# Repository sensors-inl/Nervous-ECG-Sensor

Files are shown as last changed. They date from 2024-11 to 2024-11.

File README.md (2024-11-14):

# Nervous - ECG Sensor

The **Nervous** initiative is a project embracing open-hardware and open-source
principles, with the goal of delivering wearable sensors and accompanying
software for the analysis of Autonomic Nervous System (SNA) activity.

The entire project is published under the MIT Licence.

## ECG Sensor

Contained within this repository are ECAD files for the production of PCBs and
the assembly of circuits for a wireless, wrist-worn ECG sensor.

Originally intended for measuring heart rate via electrodes positioned on the
forearms or hands, this sensor utilizes the AD8232 in conjunction with passive
components, as outlined in the "EXERCISE APPLICATION: HEART RATE MEASURED AT
THE HANDS" section on page 27 of the datasheet:
<https://www.analog.com/media/en/technical-documentation/data-sheets/ad8232.pdf>.
You have the freedom to adjust this configuration to suit different
applications and electrode placements.

The microcontroller employed is an ISP1807 (Insight SiP), which houses a
nRF52840 (Nordic Semiconductor).

## Hardware features

- USB-C connector for charging battery
- Embedded LiPo battery charger and I2C fuel-gauge
- On/Off SPST button (enables / disables voltage regulator)
- RGB status Led
- AD8232 ECG AFE featuring a 7 Hz - 24 Hz bandpass filter (56 dB @ 13 Hz) and
RLD
- BLE wireless communication

## Manufacturing and assembling

Gerber files, drill files, assembly drawings, pick-and-place files, and the
Bill of Materials (BOM) are accessible in the ```Export``` folder:

- ```Export/Manufacturing```: Gerber (.gbr) and Drill files (.drl)
- ```Export/Assembly```: Assembly drawing (.pdf), pick and place files (.pos),
BOM (.csv)

### PCB properties for manufacturing

|                          |                   |
| :----------------------- | :---------------: |
| Dimensions               | 21.5 mm x 33.5 mm |
| Number of layers         | 2                 |
| Minimal insulation width | 0.150 mm          |
| Minimal trace width      | 0.150 mm          |
| Miniaml hole size        | 0.200 mm          |

## Modification

The ```Source``` folder holds the original KiCad project, designed using KiCad
version 7.0.8.

## Note on cables and electrodes placement

This sensor is designed to capture ECG signals across various conditions while minimizing discomfort for the subject.
To achieve this, it incorporates high gain to accommodate electrode placement on the hands or forearms, where signal strength is typically lower.
However, this positioning also amplifies sensitivity to motion artifacts, which can interfere with accurate heart beat detection.
To mitigate the impact of these artifacts, we recommend utilizing solid gel electrodes like the 3M 2650.
For connectivity, we implemented a simple 2.54 mm, 3-way header on the sensor, allowing for custom electrode connections.
It's advised to use short cables for connecting the two electrodes in proximity to the device (RLD and RA), and a longer cable for the third electrode on the opposite arm (LA).
We constructed cables featuring female crimp terminals on the sensor end and 3 mm banana plugs with a snap adapter on the electrode end.
Finally, securely hold the electrodes in place, along with the cables near the electrodes, using medical tape to minimize noise from connector friction.

## Authors and contact

- Authors: Bertrand Massot, Matthieu Mesnage, Hugo Buy
- Affiliation: INSA Lyon, Ecole Centrale Lyon, Universite Claude Bernard Lyon
1, CPE Lyon, CNRS, INL UMR 5270, 69600 Villeurbanne France.
- Contact email: <bertrand.massot@insa-lyon.fr>

## Funding

This work was supported the French National Reasearch Agency (ANR) under the
grant ANR-22-CE31-0023-03 RENFORCE.

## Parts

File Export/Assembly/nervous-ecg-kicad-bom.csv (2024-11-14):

Id | Quantity | Designator | Description | Manufacturer | Manufacturer Part Number | Supplier | Supplier Part Number
1 | 1 | BT1 | BATT LI-PO 3.7V 165MAH | BAK TECHNOLOGY | LP-402025-1S-3 | FARNELL | 2077885
2 | 5 | C1, C2, C6, C8, C9 | CAP CER 1UF 10V X5R 0402 | Yageo | CC0402KRX5R6BB105 | Farnell | 1458896
3 | 2 | C3, C4 | CAP CER 4.7UF 6.3V X5R 0402 | Yageo | CC0402KRX5R5BB475 | Farnell | 3369135
4 | 1 | C5 | CAP CER 0.47UF 10V X5R 0402 | Yageo | CC0402KRX5R6BB474 | Farnell | 3369138
5 | 3 | C7, C11, C13 | CAP CER 0.1UF 16V X7R 0402 | Yageo | CC0402JRX7R7BB104 | Farnell | 3369125
6 | 1 | C10 | CAP CER 1000PF 50V X7R 0402 | Yageo | CC0402KRX7R9BB102 | Farnell | 3019380
7 | 2 | C12, C14 | CAP CER 0.22UF 10V X5R 0402 | Yageo | CC0402KRX5R6BB224 | Farnell | 9402055
8 | 1 | C15 | CAP CER 22000PF 16V X7R 0402 | Yageo | CC0402KRX7R7BB223 | Farnell | 3019299
9 | 1 | C16 | CAP CER 3300PF 50V X7R 0402 | Yageo | CC0402KRX7R9BB332 | Farnell | 3873402
10 | 1 | D1 | DIODE SCHOTTKY 20V 500MA SOD123 | STMicroelectronics | STPS0520Z | FARNELL | 1467545
11 | 2 | D4, D5 | LED RGB CLEAR 4SMD | KINGBRIGHT | APHF1608LSEEQBDZGKC | DIGIKEY | 754-2143-1-ND
12 | 1 | F1 | PTC RESET FUSE 16V 500MA 1210 | BEL | 0ZCH0050FF2G | Farnell | 2848519
13 | 1 | J1 | CONN RCP USB3.1 TYPEC 24P SMD RA | MOLEX | 105450-0101 | FARNELL | 2524076
14 | 1 | J2 | MOLEX 53048-0310 | MOLEX | 53048-0310 | FARNELL | 9732918
15 | 1 | J4 | CONN HEADER R/A 4POS 2.54MM | AMPHENOL COMMUNICATIONS SOLUTIONS | 77315-118-04LF | FARNELL | 3728851
16 | 1 | R1 | RES SMD 3K OHM 1% 1/16W 0402 | Yageo | AC0402FR-073KL | Farnell | 3951323
17 | 1 | R3 | RES 5.9K OHM 1% 1/16W 0402 | Yageo | RC0402FR-075K9L | Farnell | 3951010
18 | 6 | R5, R6, R7, R8, R10, R14 | RES 10K OHM 1% 1/16W 0402 | Yageo | RC0402FR-0710KL | Farnell | 9239359
19 | 1 | R9 | RES 0.01 OHM 1% 1/10W 0603 | Yageo | RL0603FR-070R01L | Farnell | 8067767
20 | 5 | R11, R12, R13, R18, R19 | RES SMD 10M OHM 1% 1/16W 0402 | Yageo | RC0402FR-0710ML | Farnell | 1458733
21 | 2 | R15, R16 | RES SMD 180K OHM 1% 1/10W 0402 | Panasonic | ERJ-H2RF1803X | Farnell | 3644222
22 | 1 | R17 | RES SMD 360K OHM 1% 1/16W 0402 | Yageo | RC0402FR-07360KL | Digi-Key | 311-360KLRCT-ND
23 | 3 | R20, R21, R27 | RES SMD 1M OHM 1% 1/16W 0402 | Yageo | RC0402FR-071ML | Farnell | 9239588
24 | 3 | R22, R24, R30 | RES 1K OHM 1% 1/16W 0402 | Yageo | RC0402FR-071KL | Farnell | 9239235
25 | 2 | R23, R25 | RES 100K OHM 1% 1/16W 0402 | Yageo | RC0402FR-07100KL | Farnell | 9239472
26 | 2 | R26, R32 | RES 4.7K OHM 1% 1/16W 0402 | Yageo | RC0402FR-074K7L | Farnell | 9239316
27 | 1 | R28 | RES 5.1K OHM 0.5% 1/10W 0402 | PANASONIC | ERJ-U2RD5101X | FARNELL | 3516311
28 | 1 | R29 | RES 5.1K OHM 0.5% 1/10W 0402 | PANASONIC | ERJ-U2RD5101X | FARNELL | 3516311
29 | 1 | U1 | RF TXRX MODULE BT TRACE ANT SMD | INSIGHT SIP | ISP1807-LR-RS | DIGIKEY | 1786-1019-1-ND
30 | 1 | U2 | IC BATT CHG LI-ION 1CELL 16QFN | TEXAS INSTRUMENTS | BQ24074RGTT | FARNELL | 3123775
31 | 1 | U3 | IC BATT FUEL GAUGE LICOO2 12SON | TEXAS INSTRUMENTS | BQ27441DRZR-G1A | FARNELL | 3123775
32 | 1 | U4 | IC REG LINEAR 3.3V 200MA SOT23-5 | TEXAS INSTRUMENTS | TPS7A0533PDBVR | DIGIKEY | 296-TPS7A0533PDBVRDKR-ND
33 | 1 | U5 | IC ECG FRONT END 20LFCSP | Analog Devices | AD8232ACPZ-R7 | Farnell | 4029748
34 | 1 | U6 | IC INTFACE SPECIALIZED TSOT23-6 | ANALOG DEVICES | MAX16054AZT+T | FARNELL | 2515822
35 | 1 | U7 | SWITCH TACTILE SPST-NO 0.02A 15V | PANASONIC | EVP-AA502W | FARNELL | 2831733
36 | 1 | U9 | TVS Diode WE-TVS-Standard, VRWM=5.0V | SEMTECH | SM05.TCT | Farnell | 1456392
37 | 1 | U10 | LIGHTPIPE PNL MT CONVEX 0.250" | DIALIGHT | 515-1302-0250F | FARNELL | 3775816

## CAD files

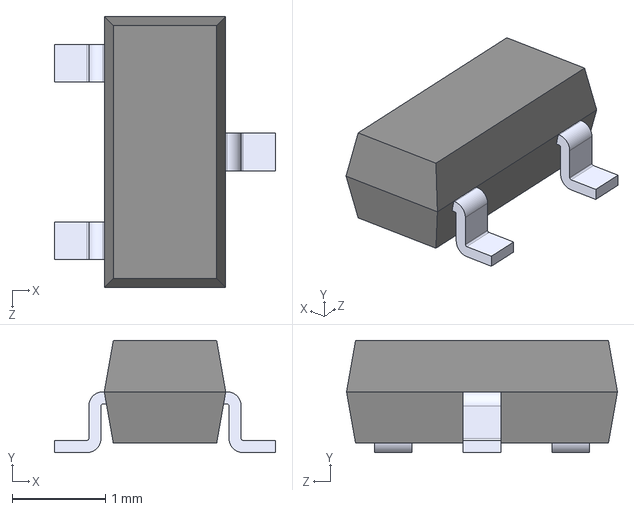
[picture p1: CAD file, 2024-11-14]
Source/nervous-ecg-3dmodels/SM05.TCT.STEP
2.37 x 1.20 x 2.90 mm

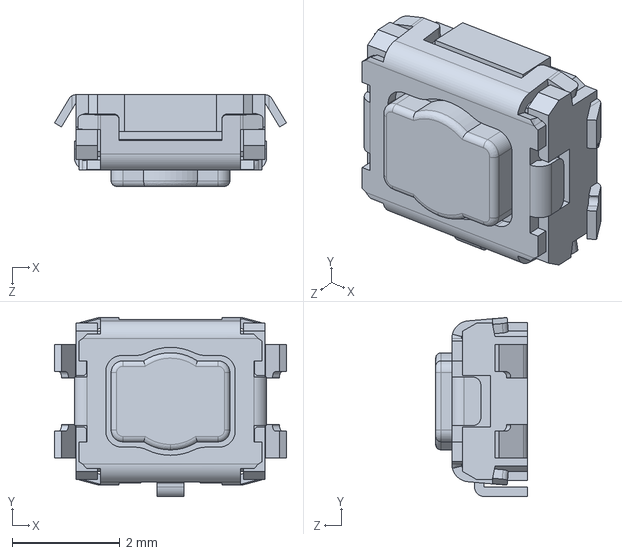
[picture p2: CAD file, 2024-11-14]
Source/nervous-ecg-3dmodels/EVPAA-102K_302K_502W_702W_902Q.STEP
4.30 x 3.32 x 1.70 mm

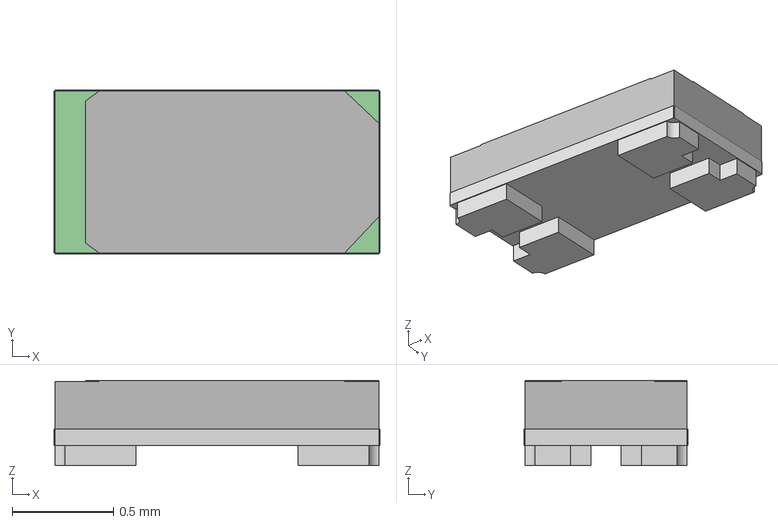
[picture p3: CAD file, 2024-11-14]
Source/nervous-ecg-3dmodels/LED_RGB_SMD_0603.step
1.61 x 0.81 x 0.42 mm

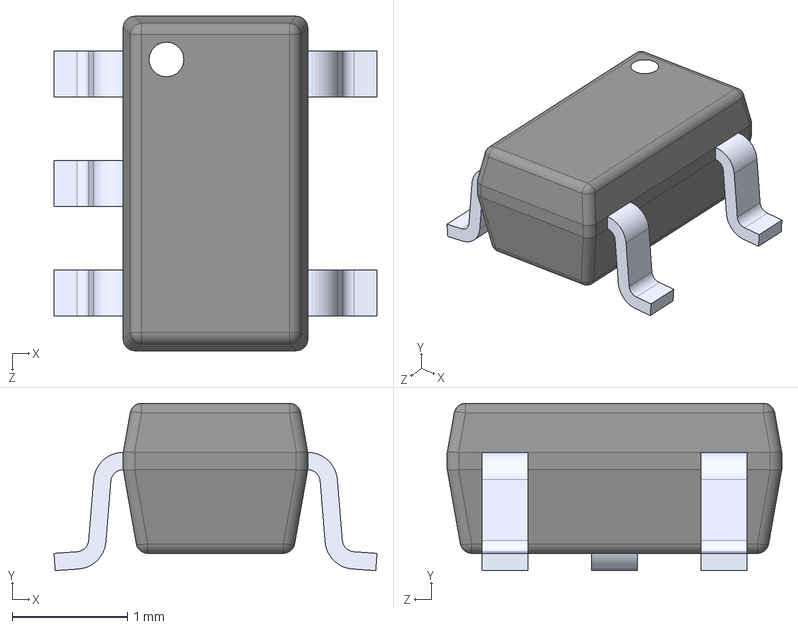
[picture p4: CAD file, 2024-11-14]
Source/nervous-ecg-3dmodels/TPS7A0533PDBVR.step
2.80 x 1.45 x 2.90 mm

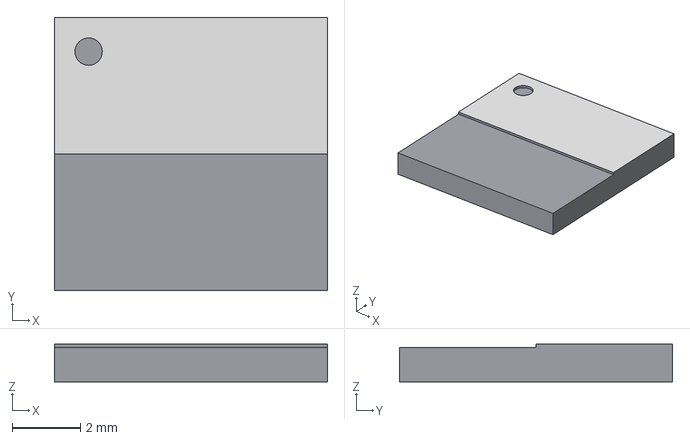
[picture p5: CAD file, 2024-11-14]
Source/nervous-ecg-3dmodels/ISP1807-LR.step
8.00 x 8.00 x 1.10 mm

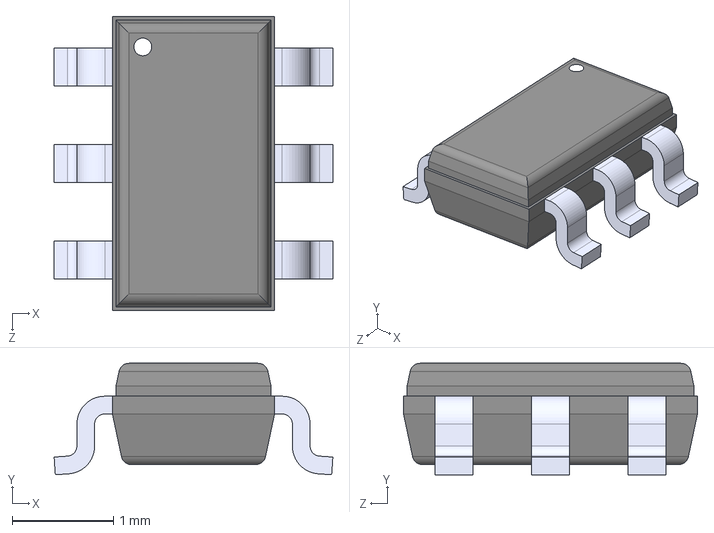
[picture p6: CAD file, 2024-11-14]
Source/nervous-ecg-3dmodels/MAX16054AZT+T.STEP
2.75 x 1.10 x 2.90 mm

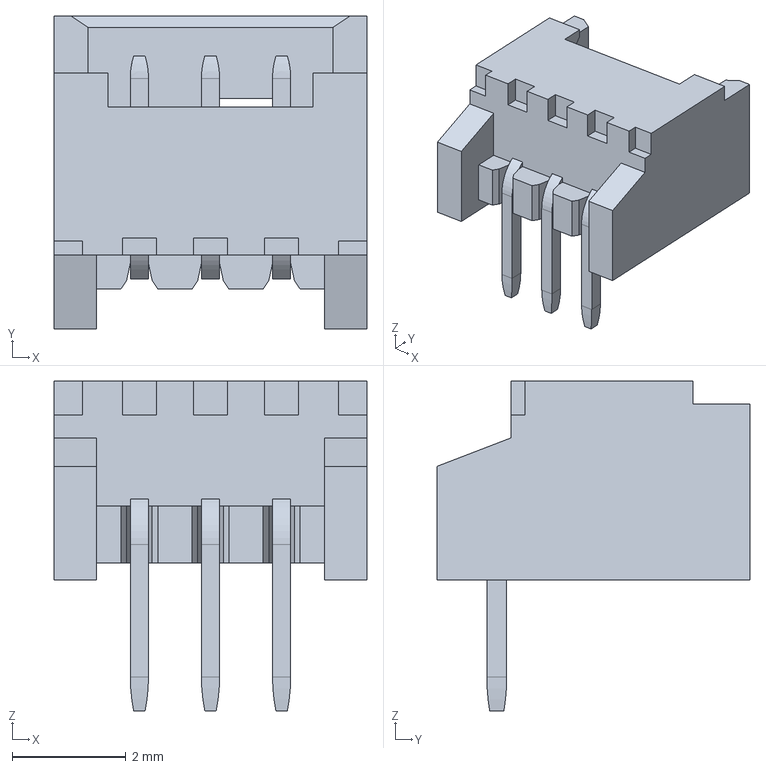
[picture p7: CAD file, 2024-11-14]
Source/nervous-ecg-3dmodels/530480310.stp
5.50 x 5.50 x 5.80 mm

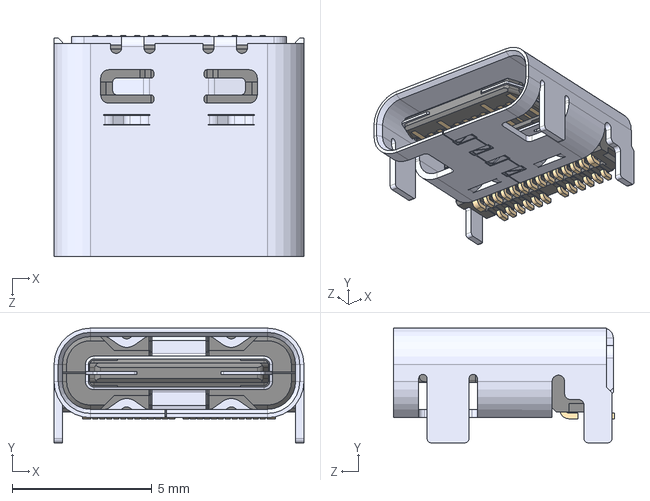
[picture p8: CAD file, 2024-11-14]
Source/nervous-ecg-3dmodels/105450-0101.step
8.94 x 4.10 x 7.90 mm

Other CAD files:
Housing/nervous-housing.f3z

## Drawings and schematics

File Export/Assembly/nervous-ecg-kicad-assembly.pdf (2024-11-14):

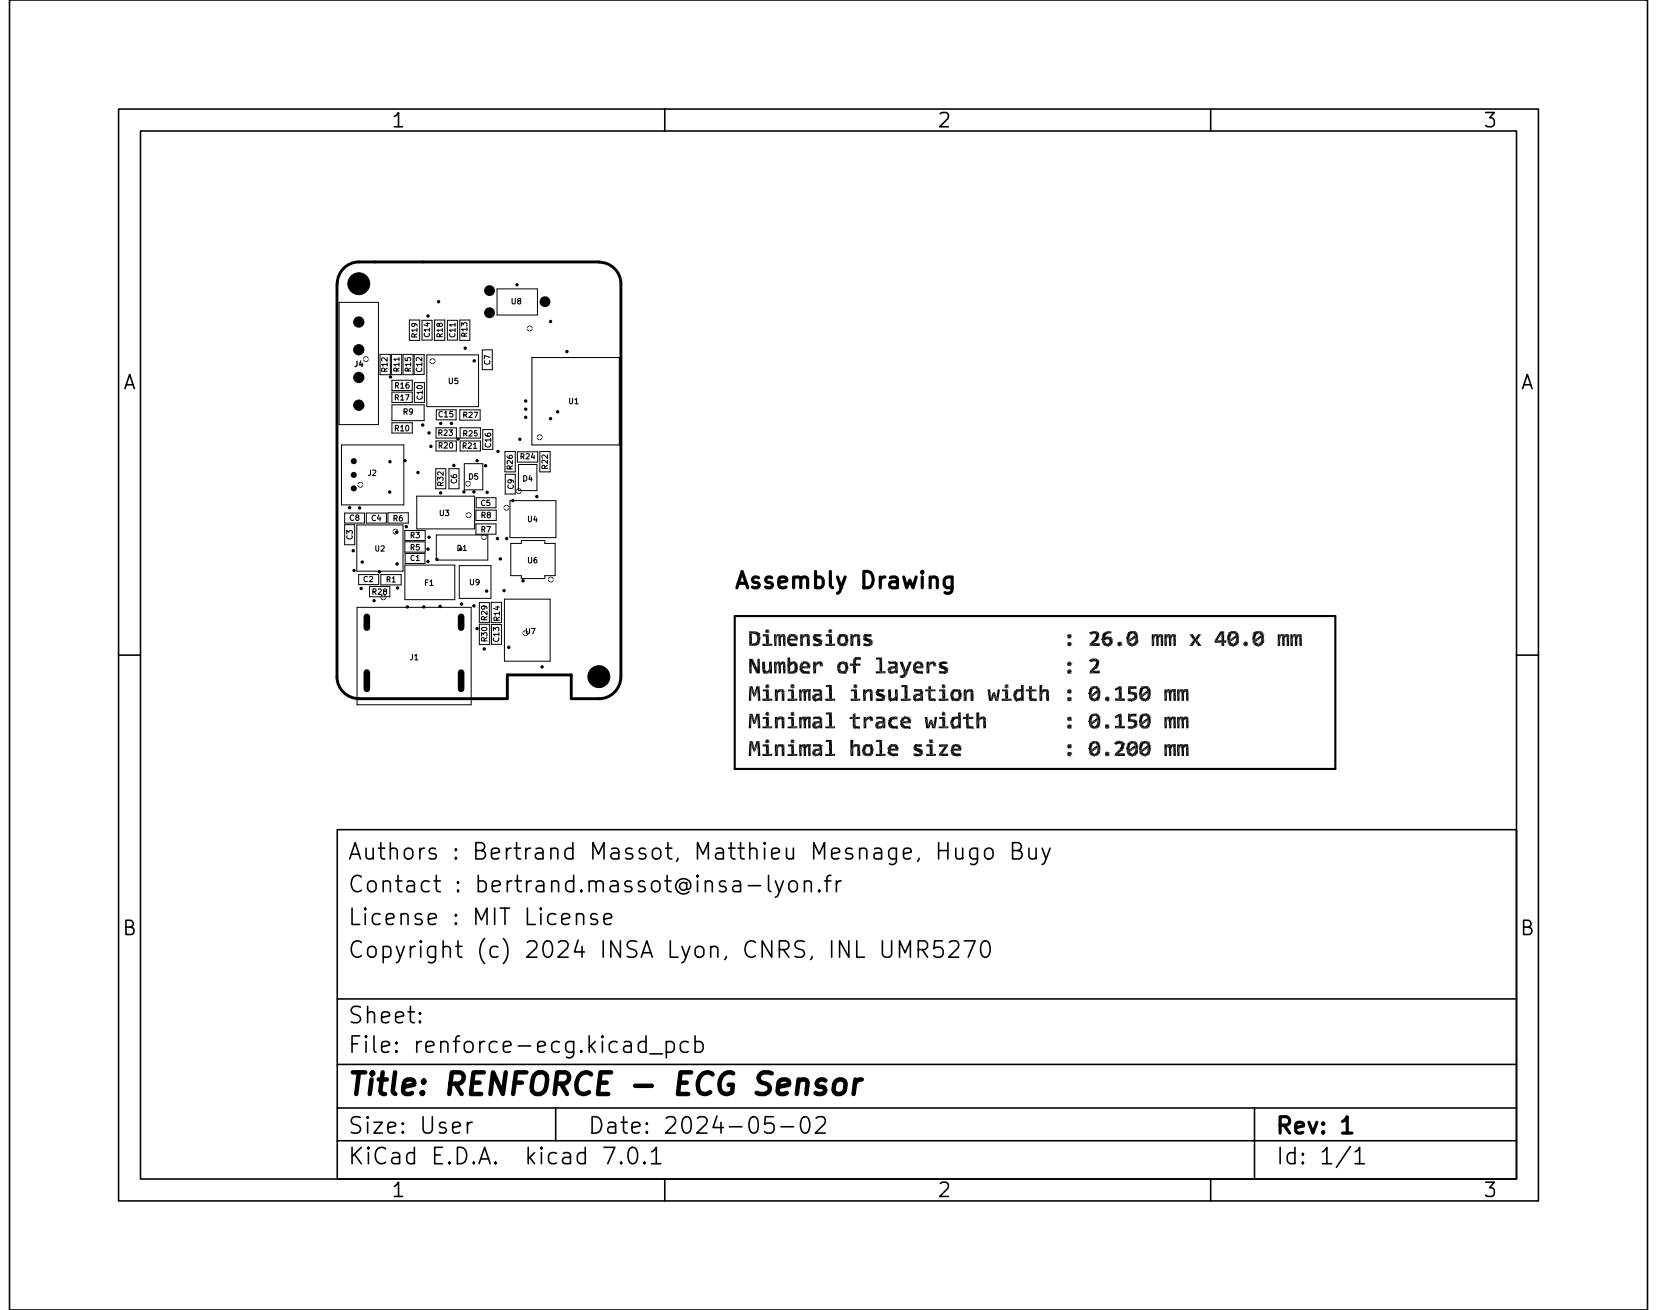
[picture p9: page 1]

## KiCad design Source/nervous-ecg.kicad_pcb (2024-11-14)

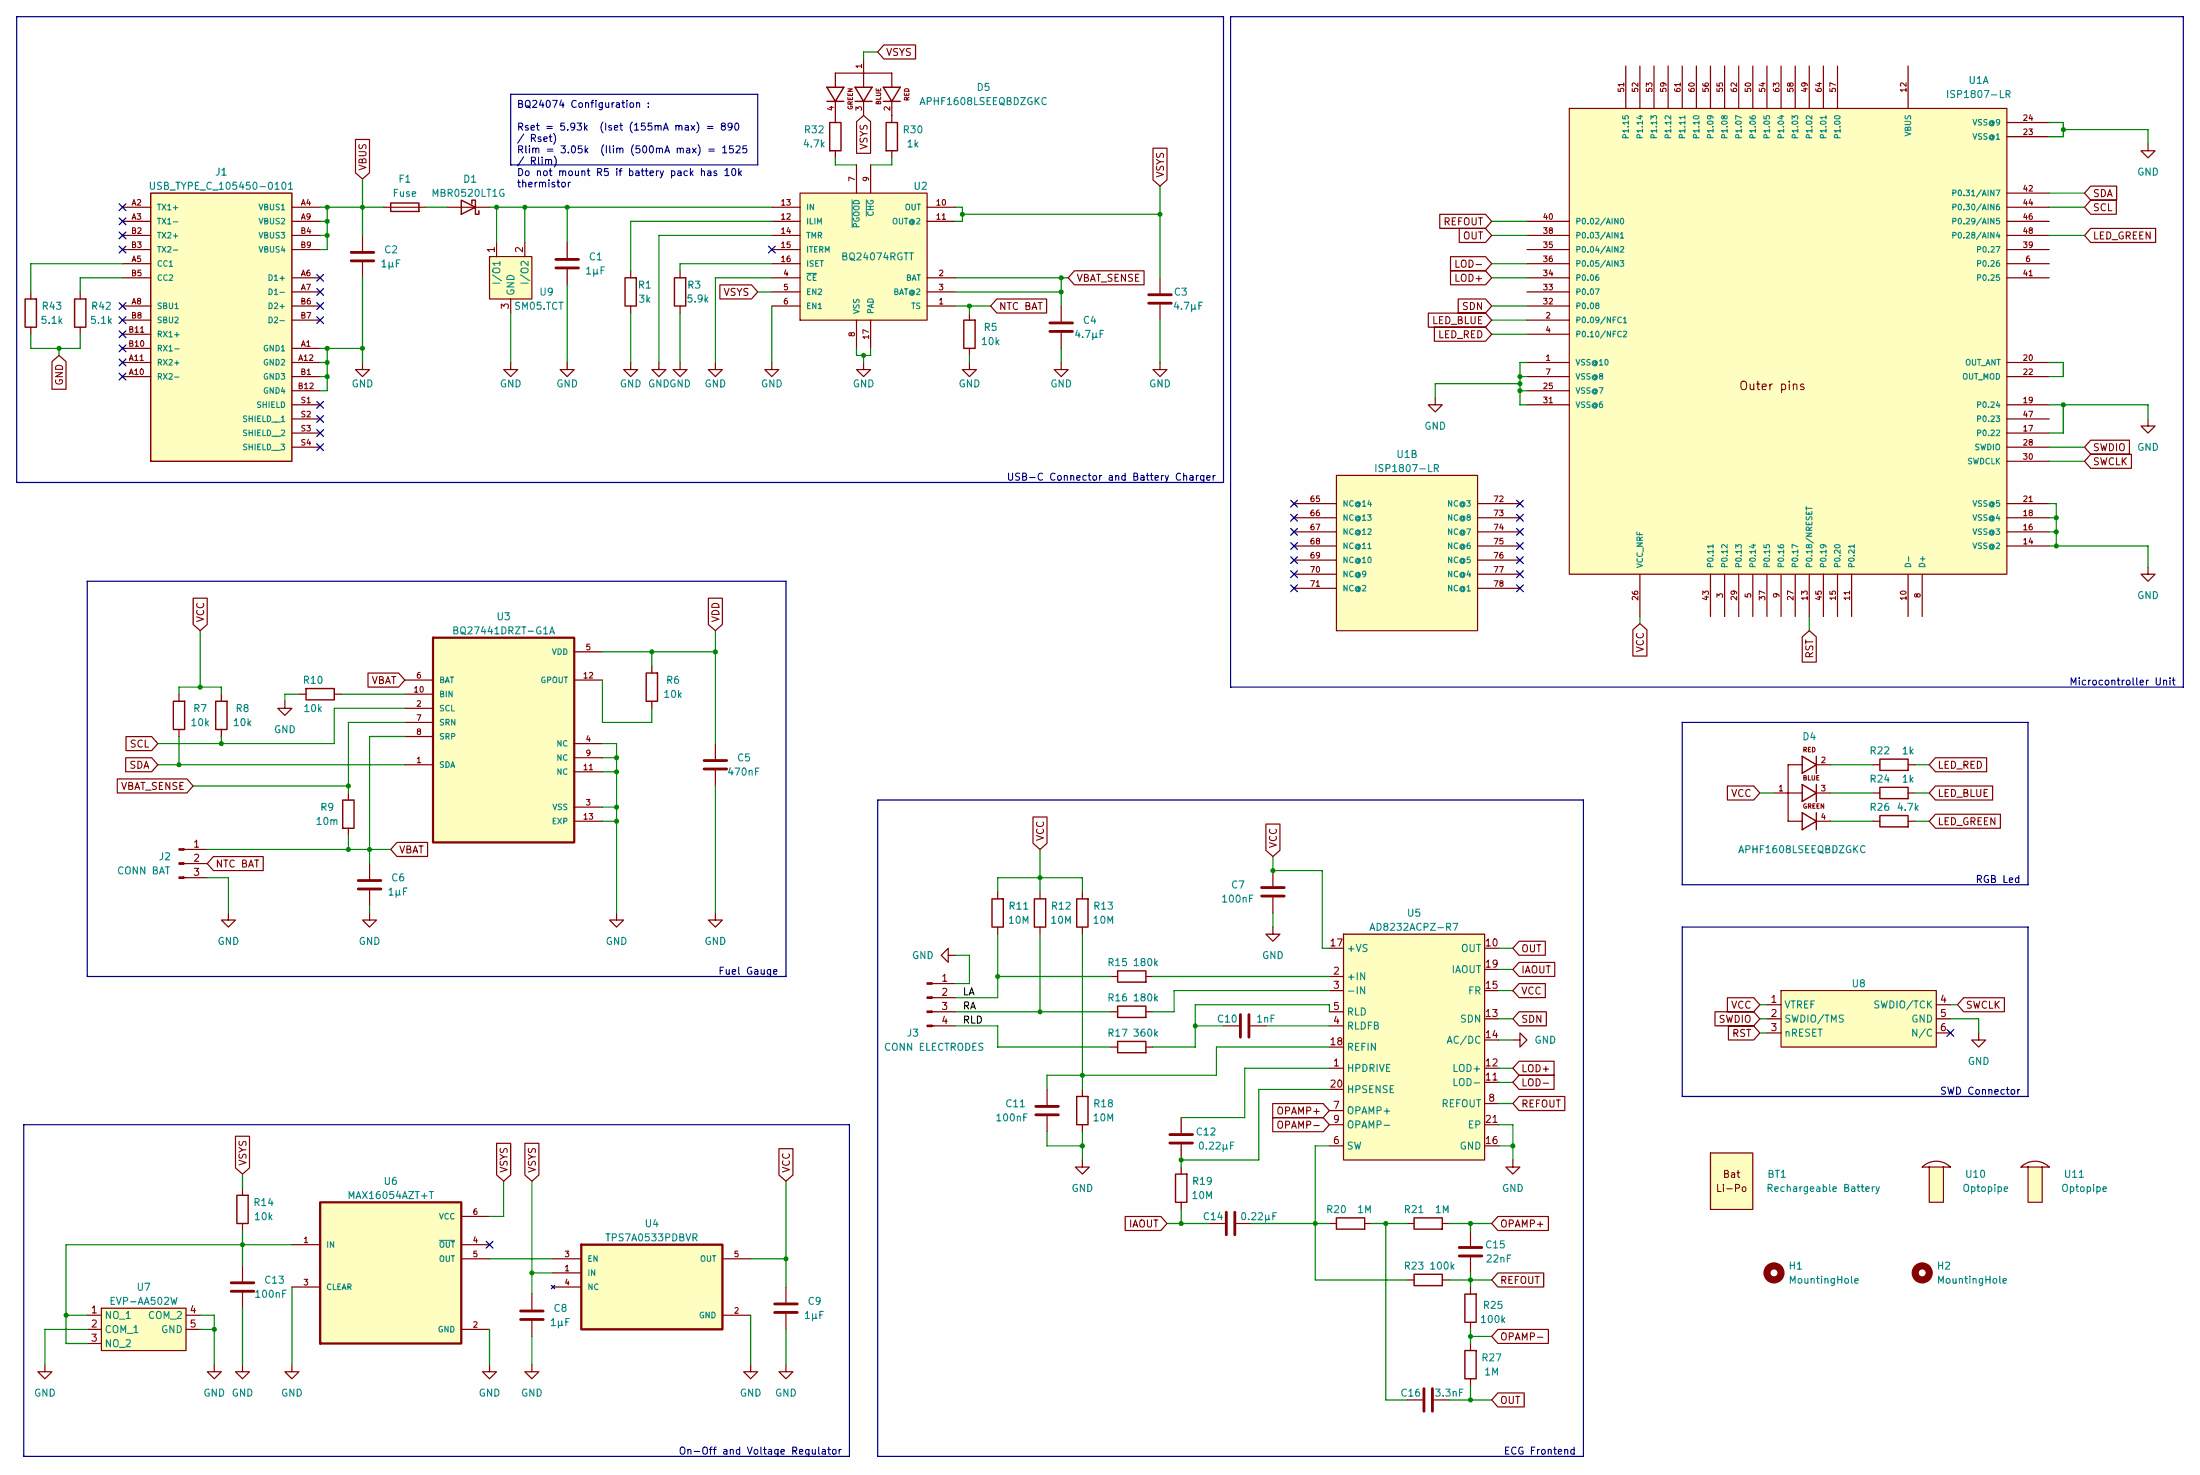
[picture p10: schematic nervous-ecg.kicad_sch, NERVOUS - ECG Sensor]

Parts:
BT1: BATT LI-PO 3.7V 165MAH; Manufacturer Part Number LP-402025-1S-3
C1, C2, C6, C8, C9: CAP CER 1UF 10V X5R 0402; C_0402_1005Metric; Manufacturer Part Number CC0402KRX5R6BB105
C3, C4: CAP CER 4.7UF 6.3V X5R 0402; C_0402_1005Metric; Manufacturer Part Number CC0402KRX5R5BB475
C5: CAP CER 0.47UF 10V X5R 0402; C_0402_1005Metric; Manufacturer Part Number CC0402KRX5R6BB474
C7, C11, C13: CAP CER 0.1UF 16V X7R 0402; C_0402_1005Metric; Manufacturer Part Number CC0402JRX7R7BB104
C10: CAP CER 1000PF 50V X7R 0402; C_0402_1005Metric; Manufacturer Part Number CC0402KRX7R9BB102
C12, C14: CAP CER 0.22UF 10V X5R 0402; C_0402_1005Metric; Manufacturer Part Number CC0402KRX5R6BB224
C15: CAP CER 22000PF 16V X7R 0402; C_0402_1005Metric; Manufacturer Part Number CC0402KRX7R7BB223
C16: CAP CER 3300PF 50V X7R 0402; C_0402_1005Metric; Manufacturer Part Number CC0402KRX7R9BB332
D1: DIODE SCHOTTKY 20V 500MA SOD123; D_SOD-123; Manufacturer Part Number STPS0520Z
D4, D5: LED RGB CLEAR 4SMD; APHF1608LSEEQBDZGKC; Manufacturer Part Number APHF1608LSEEQBDZGKC
F1: PTC RESET FUSE 16V 500MA 1210; Fuse_1210_3225Metric; Manufacturer Part Number 0ZCH0050FF2G
H1, H2: MountingHole; MountingHole_2mm
J1: CONN RCP USB3.1 TYPEC 24P SMD RA; USB_TYPE_C_105450-0101; Manufacturer Part Number 105450-0101
J2: MOLEX 53048-0310; CONN_BAT_53048-0310; Manufacturer Part Number 53048-0310
J3: CONN HEADER R/A 4POS 2.54MM; CONN_ELECTRODE; Manufacturer Part Number 77315-118-04LF
R1: RES SMD 3K OHM 1% 1/16W 0402; R_0402_1005Metric; Manufacturer Part Number AC0402FR-073KL
R3: RES 5.9K OHM 1% 1/16W 0402; R_0402_1005Metric; Manufacturer Part Number RC0402FR-075K9L
R5, R6, R7, R8, R10, R14: RES 10K OHM 1% 1/16W 0402; R_0402_1005Metric; Manufacturer Part Number RC0402FR-0710KL
R9: RES 0.01 OHM 1% 1/10W 0603; R_0603_1608Metric; Manufacturer Part Number RL0603FR-070R01L
R11, R12, R13, R18, R19: RES SMD 10M OHM 1% 1/16W 0402; R_0402_1005Metric; Manufacturer Part Number RC0402FR-0710ML
R15, R16: RES SMD 180K OHM 1% 1/10W 0402; R_0402_1005Metric; Manufacturer Part Number ERJ-H2RF1803X
R17: RES SMD 360K OHM 1% 1/16W 0402; R_0402_1005Metric; Manufacturer Part Number RC0402FR-07360KL
R20, R21, R27: RES SMD 1M OHM 1% 1/16W 0402; R_0402_1005Metric; Manufacturer Part Number RC0402FR-071ML
R22, R24, R30: RES 1K OHM 1% 1/16W 0402; R_0402_1005Metric; Manufacturer Part Number RC0402FR-071KL
R23, R25: RES 100K OHM 1% 1/16W 0402; R_0402_1005Metric; Manufacturer Part Number RC0402FR-07100KL
R26, R32: RES 4.7K OHM 1% 1/16W 0402; R_0402_1005Metric; Manufacturer Part Number RC0402FR-074K7L
R42: RES 5.1K OHM 0.5% 1/10W 0402; C_0402_1005Metric; Manufacturer Part Number ERJ-U2RD5101X
R43: RES 5.1K OHM 0.5% 1/10W 0402; R_0402_1005Metric; Manufacturer Part Number ERJ-U2RD5101X
U1: RF TXRX MODULE BT TRACE ANT SMD; ISP1807-LR; Manufacturer Part Number ISP1807-LR-RS
U2: IC BATT CHG LI-ION 1CELL 16QFN; BQ24074RGTx; Manufacturer Part Number BQ24074RGTT
U3: IC BATT FUEL GAUGE LICOO2 12SON; BQ27441DRZR-G1A; Manufacturer Part Number BQ27441DRZR-G1A
U4: IC REG LINEAR 3.3V 200MA SOT23-5; TPS7A0533PDBVR; Manufacturer Part Number TPS7A0533PDBVR
U5: IC ECG FRONT END 20LFCSP; AD8232ACPZ-R7; Manufacturer Part Number AD8232ACPZ-R7
U6: IC INTFACE SPECIALIZED TSOT23-6; MAX16054AZT+T; Manufacturer Part Number MAX16054AZT+T
U7: SWITCH TACTILE SPST-NO 0.02A 15V; EVP-AA502W; Manufacturer Part Number EVP-AA502W
U8: TC2030-MCP-NL
U9: TVS Diode WE-TVS-Standard, VRWM=5.0V; SM05.TCT; Manufacturer Part Number SM05.TCT
U10, U11: LIGHTPIPE PNL MT CONVEX 0.250"; Manufacturer Part Number 515-1302-0250F

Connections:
/LA: J3.2, R11.1, R15.1
/RA: J3.3, R12.1, R16.1
/RLD: J3.4, R17.1
GND: C1.2, C2.2, C3.1, C4.2, C5.2, C6.2, C7.2, C8.2, C9.2, C11.2, C13.2, J1.A1 (GND1), J1.A12 (GND2), J1.B1 (GND3), J1.B12 (GND4), J2.3, J3.1, R1.1, R3.1, R5.1, R10.2, R18.1, U1.1 (VSS@10), U1.7 (VSS@8), U1.14 (VSS@2), U1.16 (VSS@3), U1.17 (P0.22), U1.18 (VSS@4), U1.19 (P0.24), U1.21 (VSS@5), U1.23 (VSS@1), U1.24 (VSS@9), U1.25 (VSS@7), U1.31 (VSS@6), U2.4 (~CE), U2.6 (EN1), U2.8 (VSS), U2.14 (TMR), U2.17 (PAD), U3.3 (VSS), U3.4 (NC), U3.9 (NC), U3.11 (NC), U3.13 (EXP), U4.2 (GND), U5.14 (AC/DC), U5.16 (GND), U5.21 (EP), U6.2 (GND), U6.3 (CLEAR), U7.2 (COM_1), U7.4 (COM_2), U7.5 (GND), U8.5 (GND), U9.3 (GND); also elsewhere on the board
IAOUT: C14.2, R19.1, U5.19 (IAOUT)
LED_BLUE: R24.2, U1.2 (P0.09/NFC1)
LED_GREEN: R26.2, U1.48 (P0.28/AIN4)
LED_RED: R22.2, U1.4 (P0.10/NFC2)
LOD+: U1.34 (P0.06), U5.12 (LOD+)
LOD-: U1.36 (P0.05/AIN3), U5.11 (LOD-)
NTC BAT: J2.2, R5.2, U2.1 (TS)
unnamed: C16.2, R20.2, R21.1
unnamed: D1.2 (A), F1.2
unnamed: C1.1, D1.1 (K), U2.13 (IN), U9.1 (I/O1), U9.2 (I/O2)
unnamed: D4.2, R22.1
unnamed: D4.3, R24.1
unnamed: D4.4, R26.1
unnamed: D5.2, R30.1
unnamed: D5.4, R32.1
unnamed 19: J1.A5 (CC1); also elsewhere on the board
unnamed 20: J1.B5 (CC2); also elsewhere on the board
unnamed: U1.20 (OUT_ANT), U1.22 (OUT_MOD)
unnamed: R1.2, U2.12 (ILIM)
unnamed: R3.2, U2.16 (ISET)
unnamed: R30.2, U2.9 (~CHG)
unnamed: R32.2, U2.7 (~PGOOD)
unnamed: R10.1, U3.10 (BIN)
unnamed: R6.1, U3.12 (GPOUT)
unnamed: U4.3 (EN), U6.5 (OUT)
unnamed: R15.2, U5.2 (+IN)
unnamed: R16.2, U5.3 (-IN)
unnamed: C12.1, U5.1 (HPDRIVE)
unnamed: C12.2, R19.2, U5.20 (HPSENSE)
unnamed: C11.1, R13.1, R18.2, U5.18 (REFIN)
unnamed: C10.2, R17.2, U5.5 (RLD)
unnamed: C10.1, U5.4 (RLDFB)
unnamed: C14.1, R20.1, R23.1, U5.6 (SW)
unnamed: C13.1, R14.1, U6.1 (IN), U7.1 (NO_1), U7.3 (NO_2)
OPAMP+: C15.1, R21.2, U5.7 (OPAMP+)
OPAMP-: R25.1, R27.2, U5.9 (OPAMP-)
OUT: C16.1, R27.1, U1.38 (P0.03/AIN1), U5.10 (OUT)
REFOUT: C15.2, R23.2, R25.2, U1.40 (P0.02/AIN0), U5.8 (REFOUT)
RST: U1.13 (P0.18/NRESET), U8.3 (nRESET)
SCL: R8.1, U1.44 (P0.30/AIN6), U3.2 (SCL)
SDA: R7.1, U1.42 (P0.31/AIN7), U3.1 (SDA)
SDN: U1.32 (P0.08), U5.13 (SDN)
SWCLK: U1.30 (SWDCLK), U8.4 (SWDIO/TCK)
SWDIO: U1.28 (SWDIO), U8.2 (SWDIO/TMS)
VBAT: C6.1, J2.1, R9.2, U3.6 (BAT), U3.8 (SRP)
VBAT_SENSE: C4.1, R9.1, U2.2 (BAT), U2.3 (BAT@2), U3.7 (SRN)
VBUS: C2.1, F1.1, J1.A4 (VBUS1), J1.A9 (VBUS2), J1.B4 (VBUS3), J1.B9 (VBUS4)
VCC: C7.1, C9.1, D4.1, R7.2, R8.2, R11.2, R12.2, R13.2, U1.26 (VCC_NRF), U4.5 (OUT), U5.15 (FR), U5.17 (+VS), U8.1 (VTREF)
VDD: C5.1, R6.2, U3.5 (VDD)
VSYS: C3.2, C8.1, D5.1, D5.3, R14.2, U2.5 (EN2), U2.10 (OUT), U2.11 (OUT@2), U4.1 (IN), U6.6 (VCC)

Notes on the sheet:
BQ24074 Configuration : Rset = 5.93k (Iset (155mA max) = 890 / Rset) Rlim = 3.05k (Ilim (500mA max) = 1525 / Rlim) Do not mount R5 if battery pack has 10k thermistor
RGB Led
Fuel Gauge
USB-C Connector and Battery Charger
ECG Frontend
SWD Connector
Microcontroller Unit
On-Off and Voltage Regulator

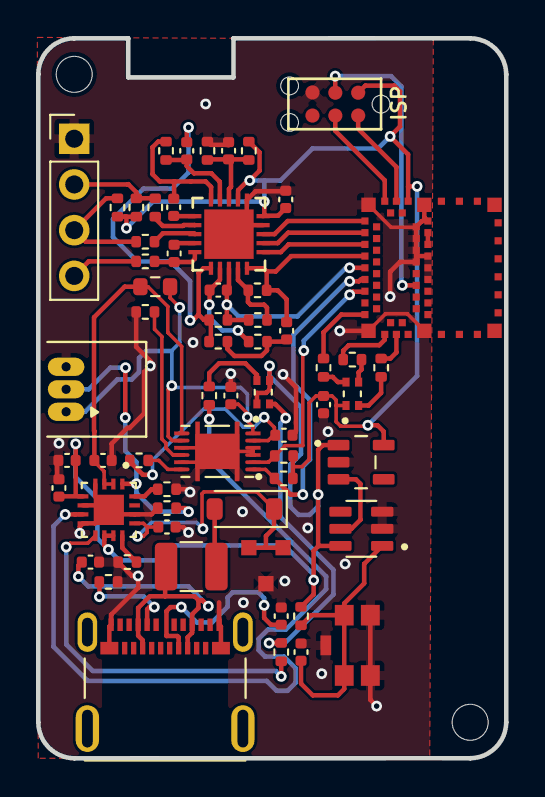
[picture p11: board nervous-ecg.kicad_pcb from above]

Board: 2 copper layers, 26.0 x 40.0 mm, 63 parts (0 on the bottom side), 54 nets.

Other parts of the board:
R28: RES 5.1K OHM 0.5% 1/10W 0402; R_0402_1005Metric
R29: RES 5.1K OHM 0.5% 1/10W 0402; C_0402_1005Metric

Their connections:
GND: R28.1, R29.1; also elsewhere on the board
unnamed 19: R28.2; also elsewhere on the board
unnamed 20: R29.2; also elsewhere on the board

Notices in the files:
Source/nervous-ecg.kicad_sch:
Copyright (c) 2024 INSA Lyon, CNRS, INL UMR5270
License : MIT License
